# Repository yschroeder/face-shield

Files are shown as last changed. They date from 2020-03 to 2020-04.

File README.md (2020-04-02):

# Print Face Shields _the fast way_
Some files and documentation on how to print the Prusa Face Shield really fast.

## Disclaimer

These design files are provided "AS IS" WITHOUT WARRANTIES OR CONDITIONS OF ANY KIND, either express or implied, including, without limitation, any warranties or conditions of TITLE, NON-INFRINGEMENT, MERCHANTABILITY, or FITNESS FOR A PARTICULAR PURPOSE.

This not a medical device. Consider it a Halloween constume! It is neither certified nor fit for any purpose.

## TL;DR

* Use `PrusaSlicer`
* Set all speeds (except for `Support material`, `Bridges`, `Gap fill`, and `First layer speed`) to your `Travel` speed. The speeds in reality are limited by the slicer automatically by the `Max. Volumetric Speed` of the filament. So the printer will not print that fast, but as fast as possible.
* Set the `Max. Volumetric Speed` of the filament to set the real print speed. With a 0.4 mm nozzle, start at 8 mm³/s, increase to find the maximum of your printer. 17 mm³/s work for a E3D V6 with 0.8mm nozzle.
* Set 0% infill
* Set 0.87 mm extrusion width when using the `stl/Covid-19 Shield v10.stl` model
* If the extruder skips steps (loud clacking noise), lower the `Max. Volumetric Speed`. Or try to increase the nozzle temp, so the filament melts faster.

## Frequently Asked Questions

Q: That `Prusa Face Shield RC3` prints so slow and the virus is spreading exponentially! How can we be faster?

A: Good point! This is exactly the purpose of this guide/repository. I will talk you through all the important things to consider when you want to print fast.

Q: Is your improved version strong enough? [Josef Prusa said on Twitter](https://twitter.com/josefprusa/status/1242931010641244161), that we should not change the design, because it needs to be beefy.

A: Actually, I don't know. Josef Prusa was not specific on why it was designed the way it was. I think the updated version is also good, it might not be as rigid, instead it is more flexible. If you think the improved version is not strong enough, there are other options. If you want to be sure, print `stl/covid19_headband_rc3_no_text v1.stl`. That version is the orignal one without the text, so it prints a bit faster while being exactly as strong and beefy.

Take a look [here](quality_control.md) to see how you can abuse the part without breaking.

Q: How much faster can we get?

A: Here are some expected printing times calculated by `PrusaSlicer` (for a Prusa i3 MK2.5 printing PETG):

* original file with `0.20mm SPEED` settings (one of the default profiles): 3:17h
* original file with settings included in `covid19_headband_rc3_1pcs.3mf` from original web page: 2:36h
* `stl/covid19_headband_rc3_no_text v1.stl` with `0.20mm SPEED` settings (one of the default profiles): 3:12h
* `stl/Covid-19 Shield v10.stl` with optimized settings: 0:43h
* `stl/Covid-19 Shield v10.stl` with optimized settings and a 0.8mm nozzle: 0:36h
* `stl/Covid-19 Shield v18.stl` with optimized settings and a 0.8mm nozzle: 0:31h

Q: I want to print overnight and do not want to get the done print every hour or so.

A: You are in luck, there is a stackable version from 2 to 9 parts. It is easily printable with a 0.4mm nozzle in about an hour per headband. Config for Slic3r: `layer: 0.25mm, all speeds to 150mm/s, bridging speed to 50mm/s, gap fill to 0mm/s, PLA, enable detect bridging perimeters`.

Q: I am using Cura to slice my STls, can you provide a guide for Cura?

A: I am afraid that at this point, I can only provide a guide for `PrusaSlicer`. By the way: Did you know that `PrusaSlicer 2.2` supports the `Ender 3` out of the box? You might want to try that!

Q: Can you provide a 888 version for A4 sheets?

A: Short answer: Good idea, a hospital also asked us for wider shields, so we did a prototype of this. Our results were mediocre at best, thus we discarded the idea and focused on the `v18` instead. Long answer: 888 punches are not close to the edge, the sheet will not bend properly around the printed part. You could solve this with extra hooks that catch the sheet at the ends. However, this would not work with thick sheets (0.8 mm) which are currently easy to buy. The wider design needs other struts, our prototype did not bend correctly so the sheet was inpossible to get on (again, 0.8 mm). We do not want to encourage you to use laser printer A4 clear sheets or laminating film! Users reported that you get headaches and vertigo after longer use. Also you cannot work on small things (dentist, stitch a wound). Especially the laminating film has bad optical properties. Further, production of injection molded parts for the original Prusa design is ramping up and sheets for the Prusa design will become common by then. Other hole layouts would be incompatible. Lastly, we found that a 297 mm wide sheet from 0.8 mm PETG is too heavy and uncomfortable. I hope these are enough reasons to not make a A4/888 version.

Q: How do I know my print is sturdy enough?

A: Look into the [Quality Control](quality_control.md) document, there we provide some hints how your part should look like, or not look like.

Q: I guess my part failed the quality control, what can I do?

A: The [Quality Control](quality_control.md) document also gives hints on what to change. Look into it again.

## Which model to print?

This repository contains multiple models that you can choose from. Let me introduce them to you:

### `stl/covid19_headband_rc3_no_text v1.stl`
This a remix of the original [Prusa Face Shield RC3](https://www.prusaprinters.org/prints/25857-prusa-face-shield). I removed the text and indents from it as it slows down printing. Otherwise, this is exactly the same as the original.

### `stl/Covid-19 Shield v18.stl` and `stl/Covid-19 Shield v10.stl`
These are versions that I designed myself. All the relevant features have the same geometry as the original Prusa version. However, the wall thickness is reduced from 2.5 mm to 1.67 mm. This makes it possible to print it very fast, but it gets more flexible (maybe this is not even a downside). The guide below uses this model.

If you have problems with layer adhesion, try `stl/Covid-19 Shield v18 Lily.stl`. It has lily pads at crucial points to help with adhesion. Just remove them with side cutters at the end.

If you want to print for longer durations (e.g. over night), you can try the stacked versions. Look into `stl/stacks`. We have stacks from 2 to 9 parts. Start with a small stack and check if it prints well on your machine and that you can split the parts afterwards!

**ATTENTION: Make sure the two perimeters stick together well! If they don't, the finished part will be extremely weak! You can try to increase the extrusion width even further (e.g. 1.0 mm) or increase the extrusion multiplier. If you cannot manage to print parts where the two wall stick to each other, print the v10 or original RC3 instead!**

### `stl/Covid-19 Shield 2.5mm v2.stl`
If you think the above version is too flimsy/flexible you can go with this one. It has the same thickness as the original from Prusa. It has a constant wall thickness of 2.5 mm.

Note: This a sturdy version of the `v10`. I will not provide a sturdy version of `v18`, as the `v18` is sturdy enough.

### `stl/Bottom Reinforcement fast MK2 v3.stl`
This is an updated version of the original bottom reinforcement part from the Prusa shield. It has no holes and constant wall thickness of 1.67 mm as well. The original one has a 1 mm gap for the plastic sheet. This one has only 0.8 mm for a tighter fit. Make sure you plastic sheets fit into this before starting mass production!

### `stl/Bottom Reinforcement light v10.stl`
This alternative to the original bottom reinforcement part prints much faster (I can print 20 in 53 minutes). It works for all sheet thicknessnes, 0.25mm, 0.5mm, and 0.75mm were already tested successfully. If you are unsure which bottom part you should print, choose this one!

Thanks to Hackbroetchen for the idea in his original design: https://www.prusaprinters.org/prints/27801-easy-and-fast-bottom_reinforcement-alternative

## Print Settings

Overall, the model we want to print is pretty simple. We do not want it to look super nice, it needs to be functional. There is basically one parameter that limits your maximum print speed: `Max. Volumetric Speed`. This parameter is defined in `mm³/s` (cubic millimeters per second) and tells `PrusaSlicer` the maximum amount of material your hotend is able to melt per second. The exact value for this depends on your hotend, nozzle size, material, print temperature, extruder gears... So you need to experiment with this a bit. In the end it boils down to this: You want your printer to extrude the maximum amount of material _all the time_. Luckily, you don't strictly need a large nozzle to achive this (but it helps). Even printers with 0.4 mm nozzles can reach their `Max. Volumetric Speed`.

There are some types of features that slow down your 3D printer. These includes gap filling small holes (or thin spaces between narrow outer perimeters), sharp turns of the printing direction and infill (which is basically sharp turns of the printing direction all the time). If you manage to print your model by only printing perimeters you can increase your print speed a lot!

The following picture shows infill (dark red) and gap fill (white). Both are slow to print.
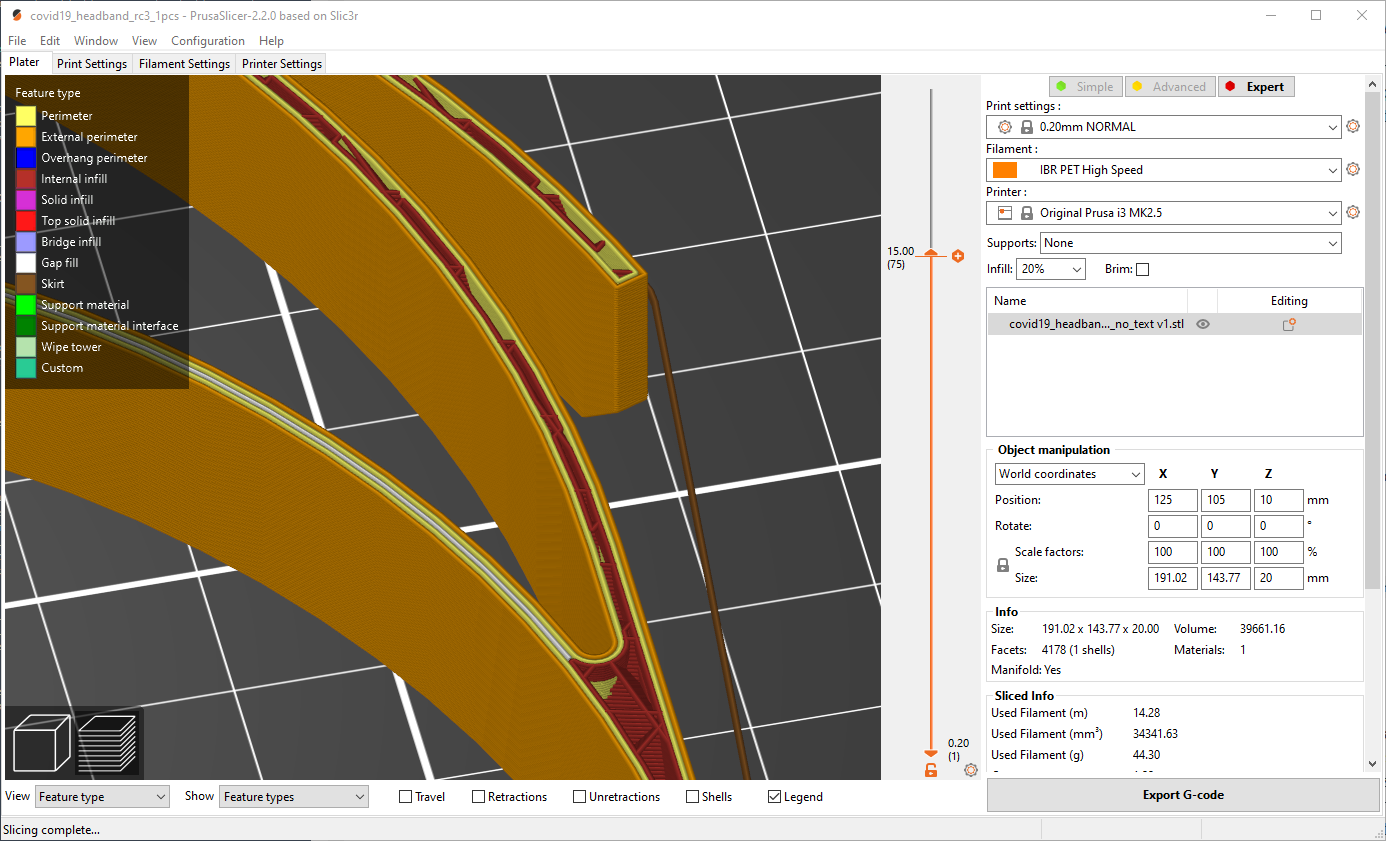
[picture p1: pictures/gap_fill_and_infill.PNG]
Gap Fill and Infill


The following picture shows a model that only consists of a single perimeter running all around the model (creating two extrusion lines). This is much faster to print (and also gives a very nice surface!).
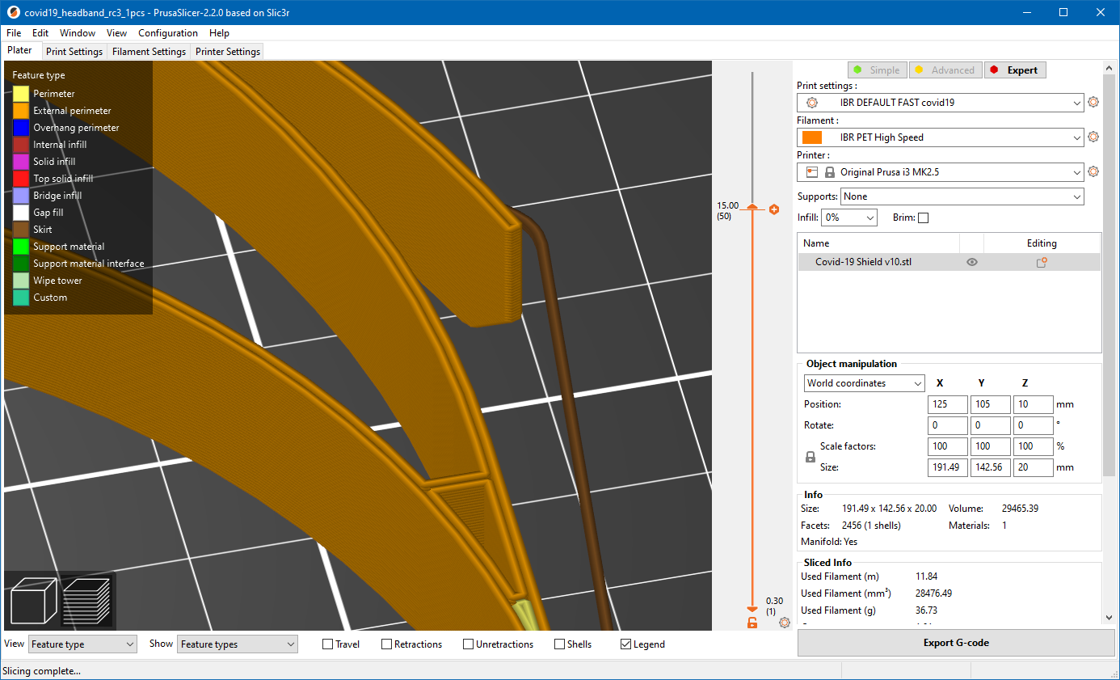
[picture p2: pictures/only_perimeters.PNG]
Only Perimeters


How can you achive this?

First, you need a model with a constant wall width and you need to know this width. The model `stl/Covid-19 Shield v18.stl` is designed to have the exact same wall thickness of 1.67 mm everywhere. If you manage that your perimeters exactly add up to 1.67 mm, no slow gap filling or infill is needed.

Second, you need to set you extrusion width correctly. Luckily, `PrusaSlicer` can help you with this. It has a function that tells you the optimal wall thickness of your model for thin wall, see the following picture:
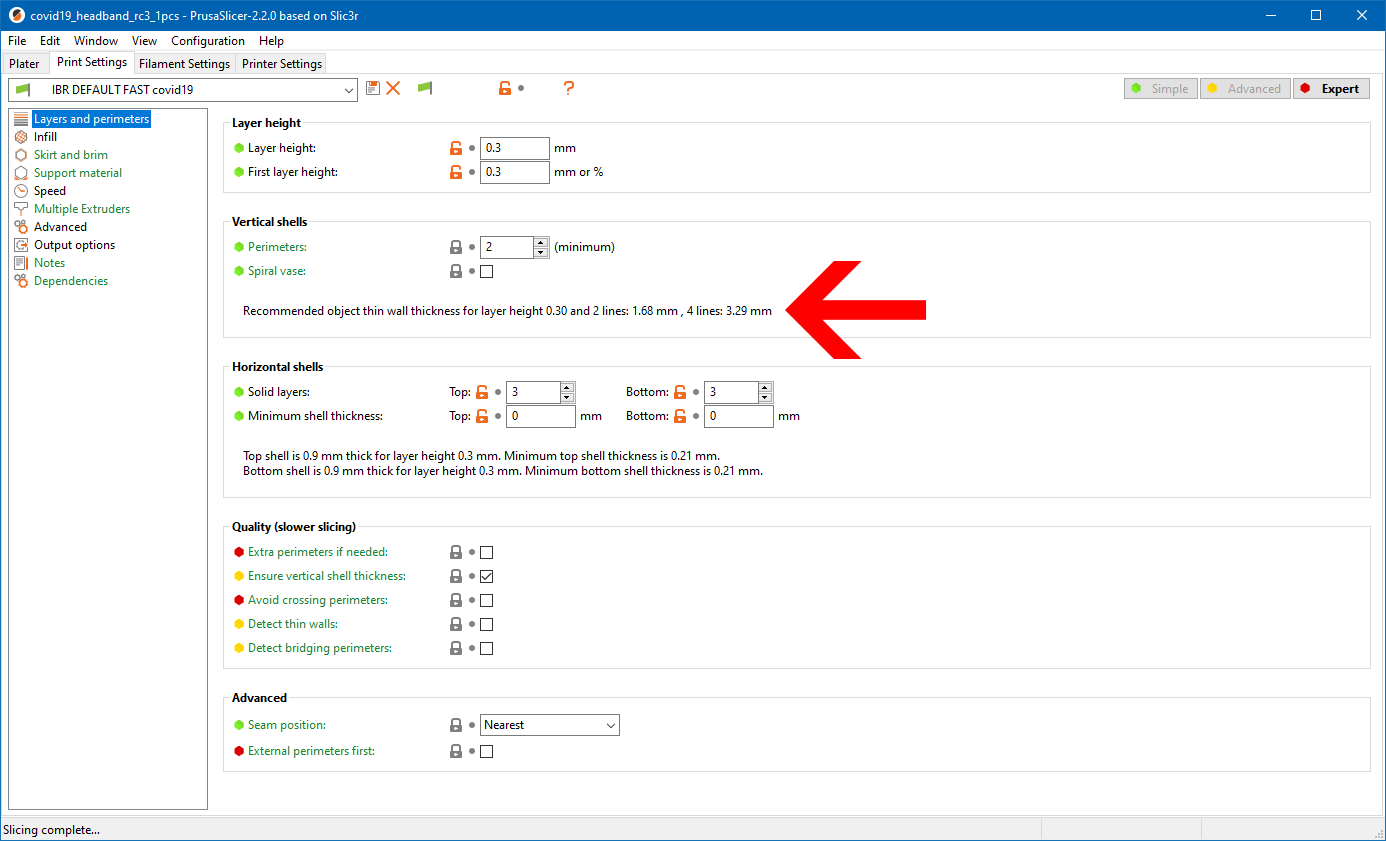
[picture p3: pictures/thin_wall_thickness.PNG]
Thin Wall Thickness


Here it says that the optimal thin wall thickness is 1.68 mm for two lines and 3.29 mm for 4 lines. 1.68 mm is very close to 1.67mm, so this is correctly configured! This value is influenced by the `Layer height` and the extrusion width for `Perimeters` and `External perimeters`. An extrusion width of 0.87 mm and a layer height of 0.3mm are used here for a 0.4 mm nozzle. Yes, you can actually print 0.87 mm width with a 0.4 mm nozzle (at least with an E3D nozzle). This [YouTube video by CNCKitchen](https://www.youtube.com/watch?v=9YaJ0wSKKHA) gives more info if you are interested.

Ok, we now have a model that is designed for this kind of print and a correct perimeter width. Let's talk about print speed. Rembember the `Max. Volumetric Speed`? This is your print speed. Configure all speeds (except for `Support material`, `Bridges`, and `Gap fill` and `First layer speed`) to your `Travel` speed. Yes, do this. You won't reach these speeds anyway (and if you actually do, can I have your printer please?). Now set the `Max. Volumetric Speed` in `Filament Settings/Advanced` to a low starting value. 8 mm³/s is a good starting point.

Let's quickly go through some other settings that can increase your print speed: The model we are printing does not need any infill. You can safely set it to 0%. Only the hooks for the rubber band would get some and they don't need it. Also, you can disable gap filling completely. Yes, this ends up with some small holes, but saves quite some time. Also it might reduce stringing, as sometimes the gap fill material does not fit into its hole and squeezes out. Disable gap fill by setting the `Gap fill` speed to 0.

Now go to the `Plater` tab and slice your model. In the bottom left corner, change the `View` to `Volumetric flow rate`. You model should have the maxum flow rate (8 mm³/s) everywhere (expect for the first layer) like in this picture:
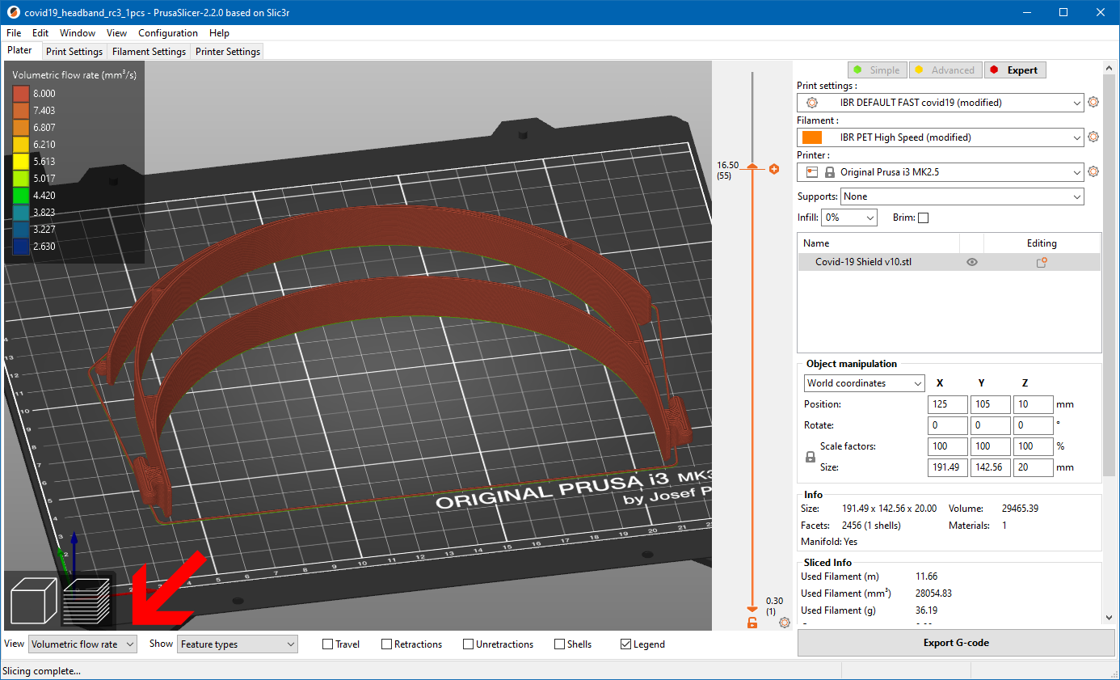
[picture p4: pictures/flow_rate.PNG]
Flow Rate


You should now be good to go for your first test print with high speed settings. If this works well (and I hope it does, otherwise this guide might be crap...) you can increase the `Max. Volumetric Speed` (e.g. in steps of 2 mm³/s) until your print starts to look ugly or your extruder makes painful noises and loses steps. If this happens, you have reached the limit of your printer. Go down to the last working value (I am running a Prusa i3 MK2.5S with a 0.8 mm nozzle at 17 mm³/s).

## Advanced Parameter Tuning

Ok, you got the basic fast print working, but you want more!

You can tune the amount of `Solid layers` at the top to close holes in the top layer of hooks for the rubber band. Increase the number of solid layers to 5. It also helps to set the `Solid infill` and `Top solid infill` to 0.55 mm, to close even more holes.

You can also tune the K factor (also known as linear advance) for your printer. Make sure it supports it. Prusa printers do support this. It will basically control the pressure in the nozzle. This is important at high speeds. You can read more about this in the [Prusa Knowledge Base](https://help.prusa3d.com/en/article/linear-advance_2252). Prusa suggest a default of 45 for PETG. I get better results with 40 on a 0.4 mm nozzle. On my 0.8 mm nozzle I am currently using a value of 15.

[gap_fill_and_infill]: pictures/gap_fill_and_infill.PNG "Gap Fill and Infill"

[only_perimeters]: pictures/only_perimeters.PNG "Only Perimeters"

[thin_wall_thickness]: pictures/thin_wall_thickness.PNG "Thin Wall Thickness"

[flow_rate]: pictures/flow_rate.PNG "Flow Rate"

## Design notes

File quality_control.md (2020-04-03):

# Quality control for face shields

Welcome to the quality control section! You being here indicates that you actually care about what you print. Congratulations!

**ATTENTION: THESE TESTS ONLY APPLY TO THE `v18` SHIELD! OTHER VERSIONS ARE LESS FLEXIBLE AND WILL POSSIBLY BREAK EARLIER!**

## What your part should look like

Actually, we can't really tell you what your printed part needs to withstand. We can only show you what our parts withstand. If your part breaks earlier, this does not automatically mean it is bad, but it is not as good as it could be! **Our part in the pictures is made from PETG, so if your part is from another material your results might be different.**

To check your part, bend it the following ways, **during bending it should not crack at all!**

Put your part on a table and press the tabs for the plastic sheet down:
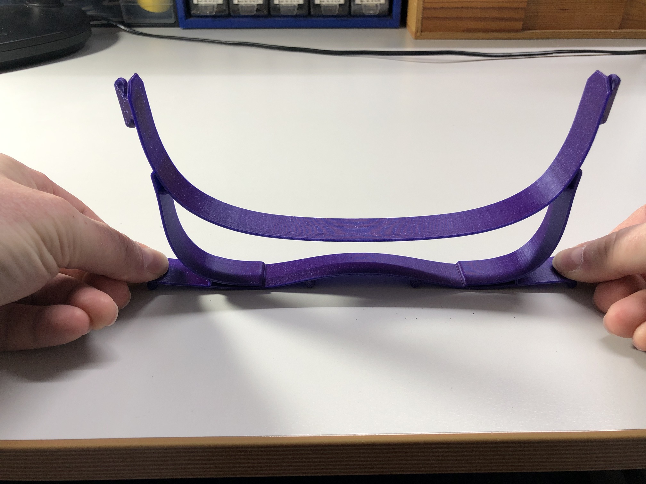
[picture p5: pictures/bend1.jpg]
Bend 1


Bend the rubber band hooks all the way to each other:
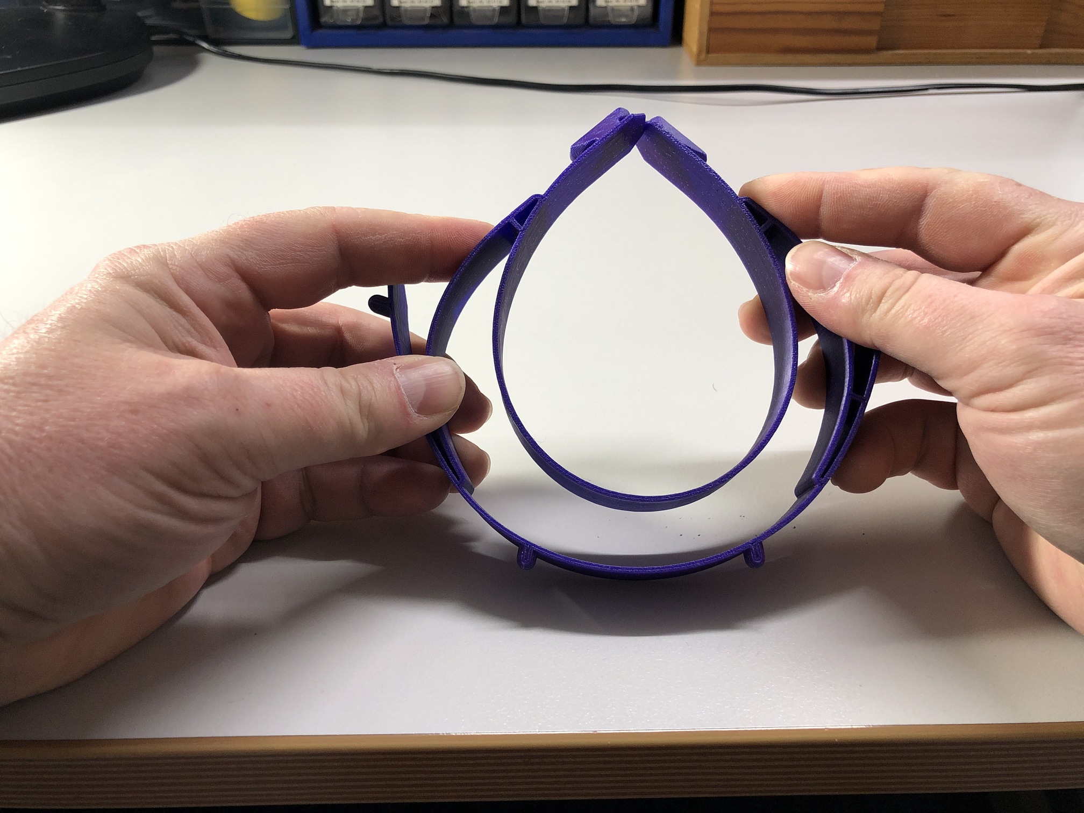
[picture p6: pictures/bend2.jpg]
Bend 2


Bend the two sides at 90° angle **in both directions multiple times**:
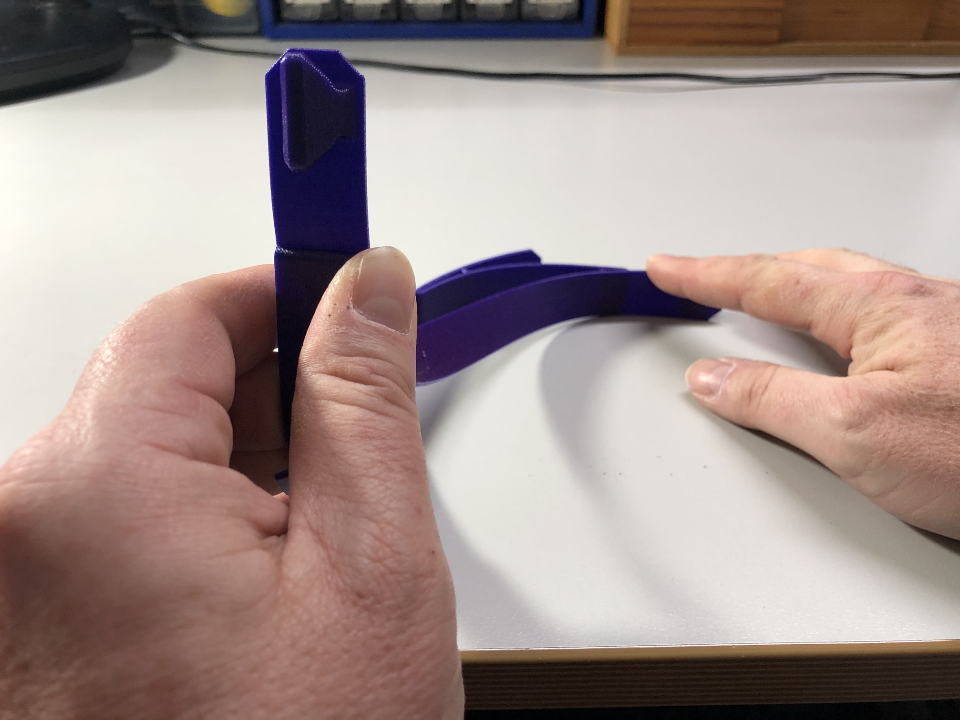
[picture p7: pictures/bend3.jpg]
Bend 3

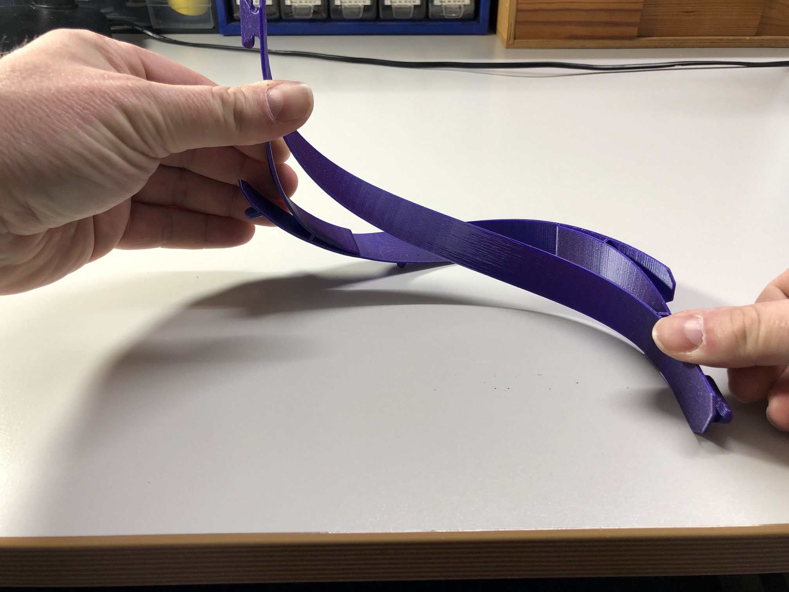
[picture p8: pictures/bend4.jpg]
Bend 4


Bend the two sides across each other:
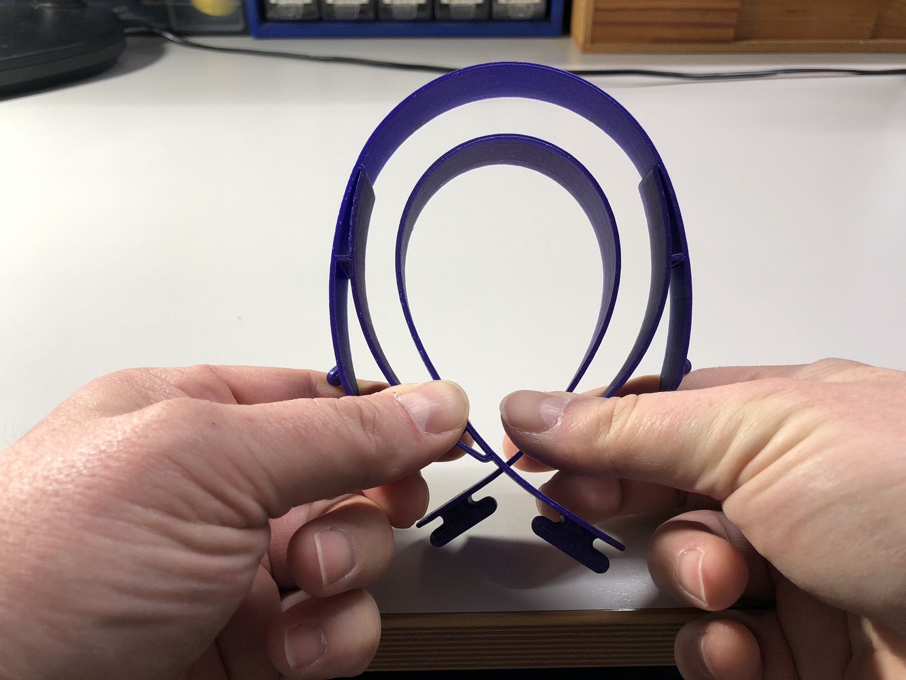
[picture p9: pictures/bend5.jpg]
Bend 5


[Here](https://cloud.stratum0.org/index.php/s/fAjpCAXFLmFsxLq?path=%2FMaterialtest%20Videos) you can find a video that shows how a PLA part can be abused if printed properly (file `PLA biegen.mp4`).

## What your part should not look like

[Here](https://cloud.stratum0.org/index.php/s/fAjpCAXFLmFsxLq?path=%2FMaterialtest%20Videos) you can find a video that shows how a good part looks in comparison to a bad part (file `qualitätstest.MOV`).

### Gaps

This part contains gaps (top two red arrows) which lead to the crumbling in the video shown above:
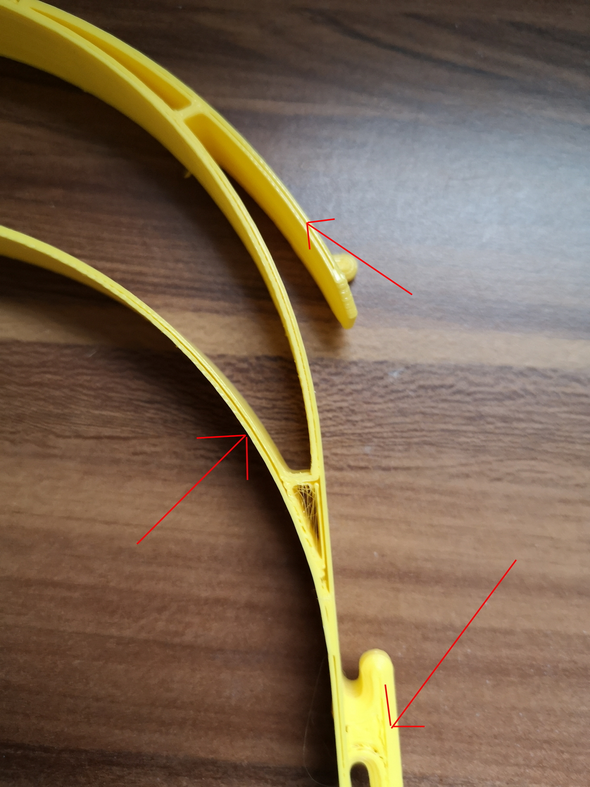
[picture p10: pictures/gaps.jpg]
Gaps


You have two options to close these gaps: In `PrusaSlicer` you can increase the `Extrusion width` of `External perimeters` even more (above 0.87 mm). `PrusaSlicer` will put the two shells closer together in this case (to reach the required 1.67 mm wall thickness). The other option is to increase the `Extrusion multiplier` so more material can fill the gap.

The problem indicated by the lower red arrow can be fixed by decreasing the `Extrusion width` for `Solid infill` and `Top solid infill` to 0.55 mm or less, depending on your nozzle size.

### Holes

You might also encounter holes in your part:
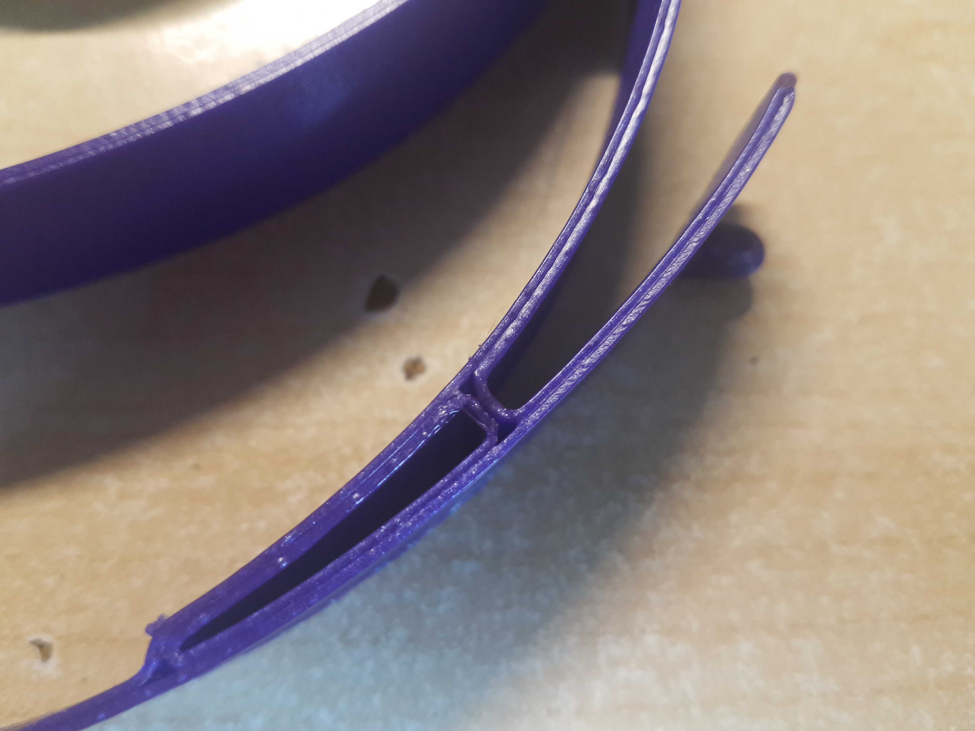
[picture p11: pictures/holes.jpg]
Holes


This effect can be reduced by increasing the `Extrusion width` of `External perimeters`. I found 1.0 mm working.

[bend1]: pictures/bend1.jpg "Bend 1"
[bend2]: pictures/bend2.jpg "Bend 2"
[bend3]: pictures/bend3.jpg "Bend 3"
[bend4]: pictures/bend4.jpg "Bend 4"
[bend5]: pictures/bend5.jpg "Bend 5"
[gaps]: pictures/gaps.jpg "Gaps"
[holes]: pictures/holes.jpg "Holes"

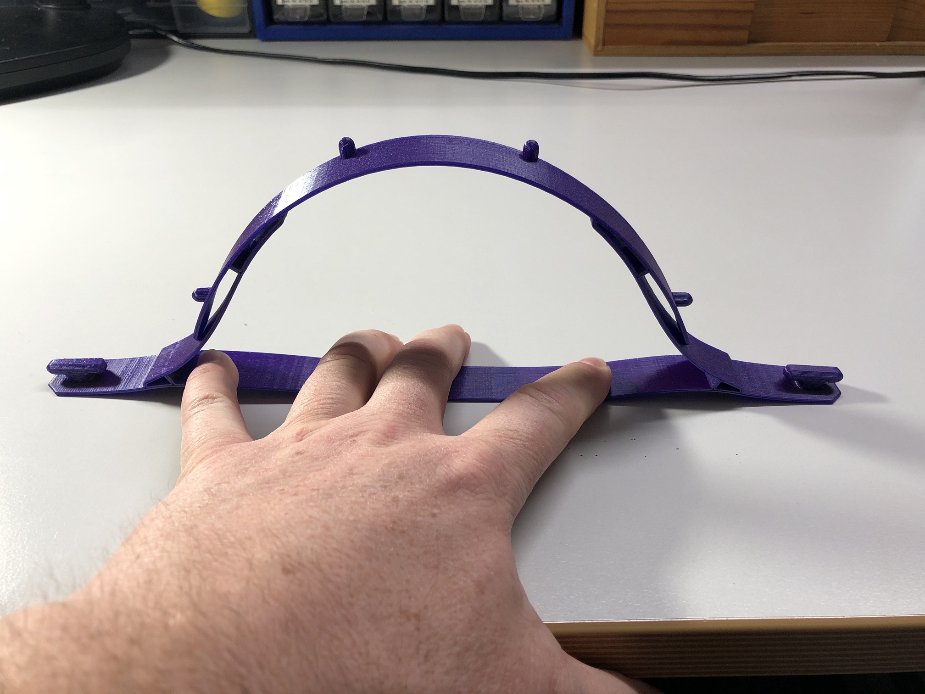
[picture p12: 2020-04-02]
pictures/bend6.jpg

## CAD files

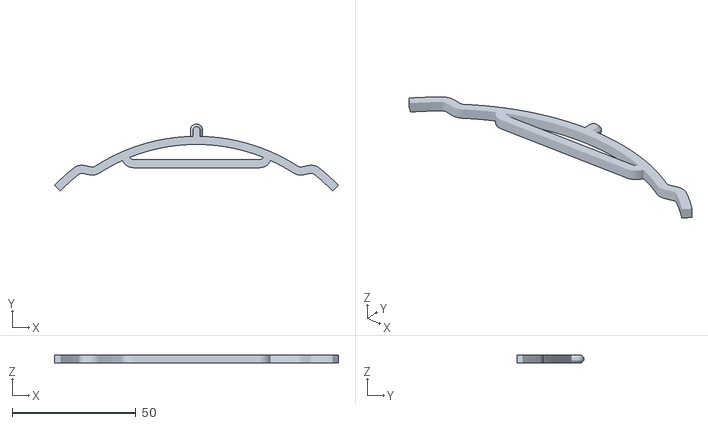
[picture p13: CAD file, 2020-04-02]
stl/Bottom Reinforcement light v10.stl
114.9 x 27.1 x 3.29

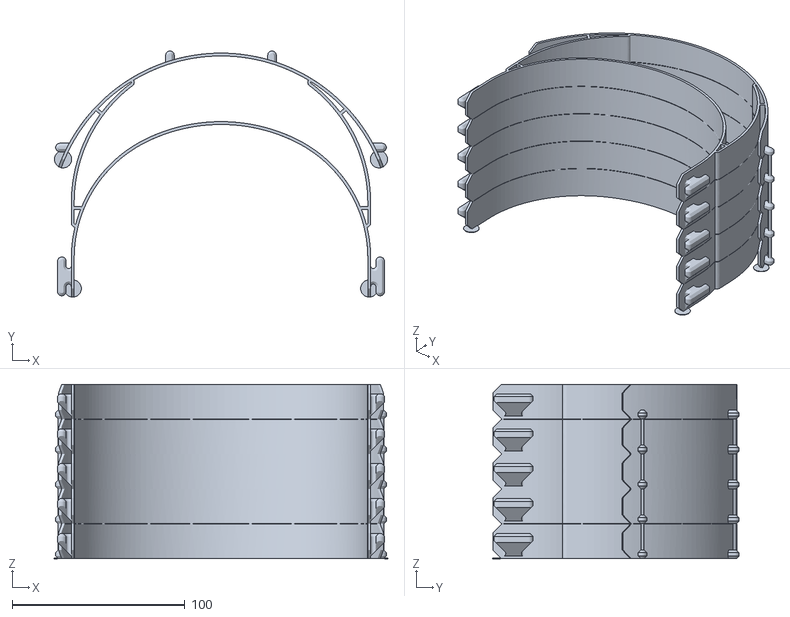
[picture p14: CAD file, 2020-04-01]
stl/stacks/v18/Covid-19 Shield v18 Stack5.stl
192.8 x 142.6 x 101.0

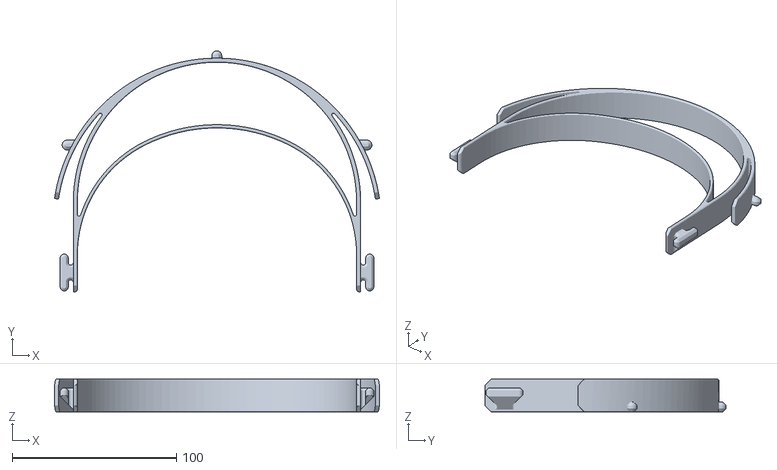
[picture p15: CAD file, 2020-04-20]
stl/US/covid19_headband_rc3us_1pc_no_text v2.stl
197.9 x 147.0 x 20.0

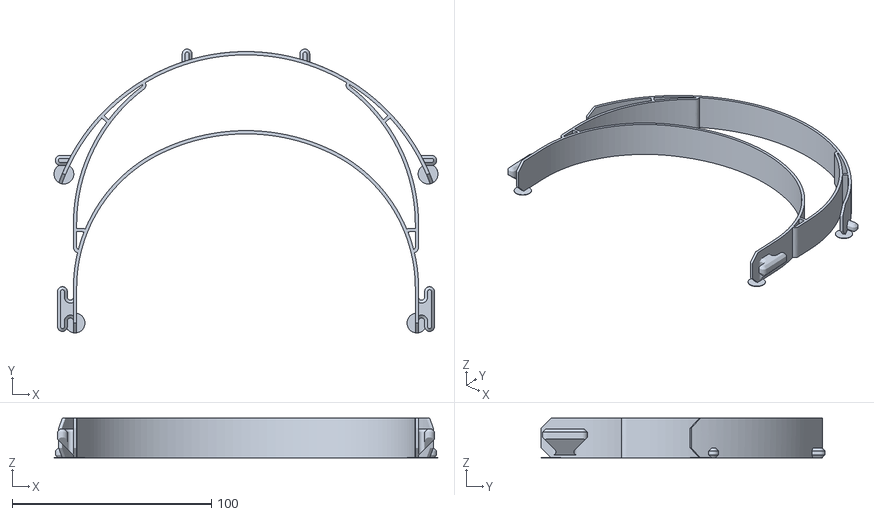
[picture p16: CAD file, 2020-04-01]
stl/Covid-19 Shield v18 Lily.stl
192.8 x 142.6 x 20.0

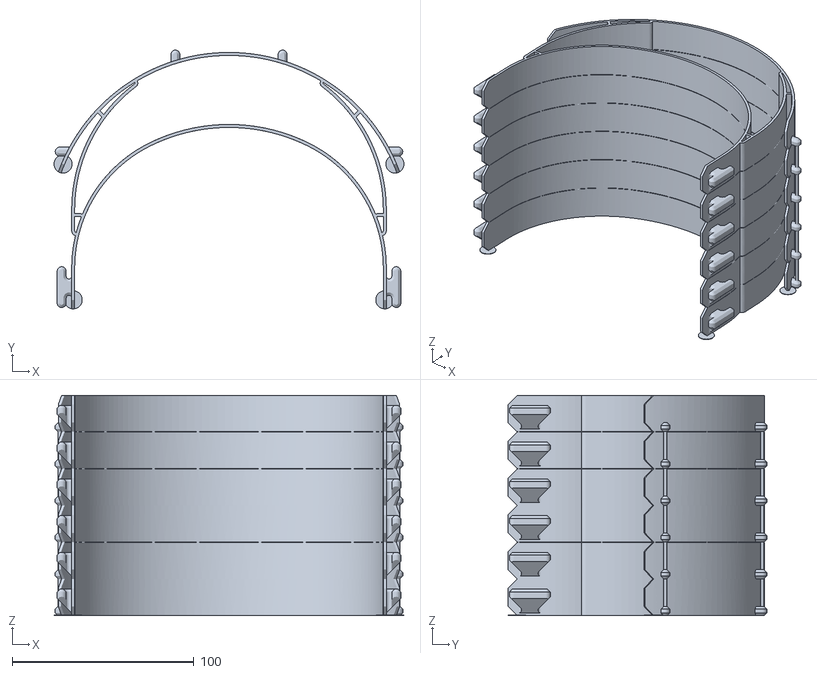
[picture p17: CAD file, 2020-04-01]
stl/stacks/v18/Covid-19 Shield v18 Stack6.stl
192.8 x 142.6 x 121.2

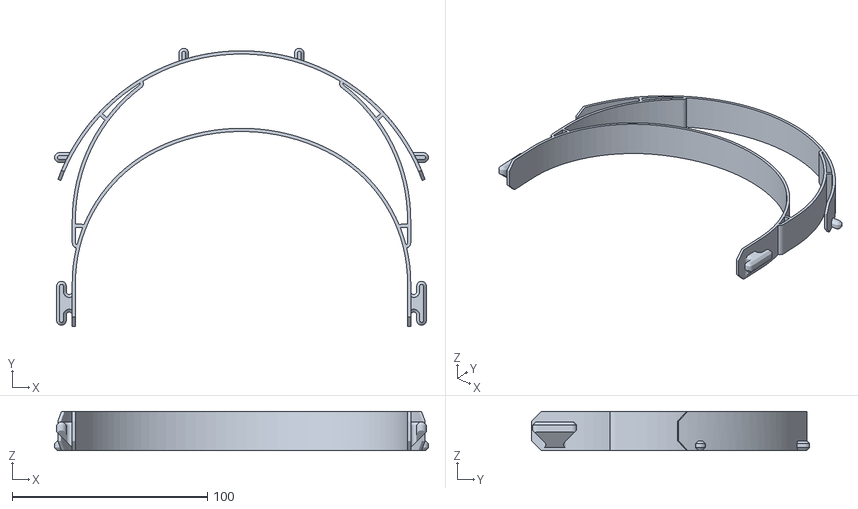
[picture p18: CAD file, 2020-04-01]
stl/Covid-19 Shield v18.stl
191.5 x 142.6 x 20.0

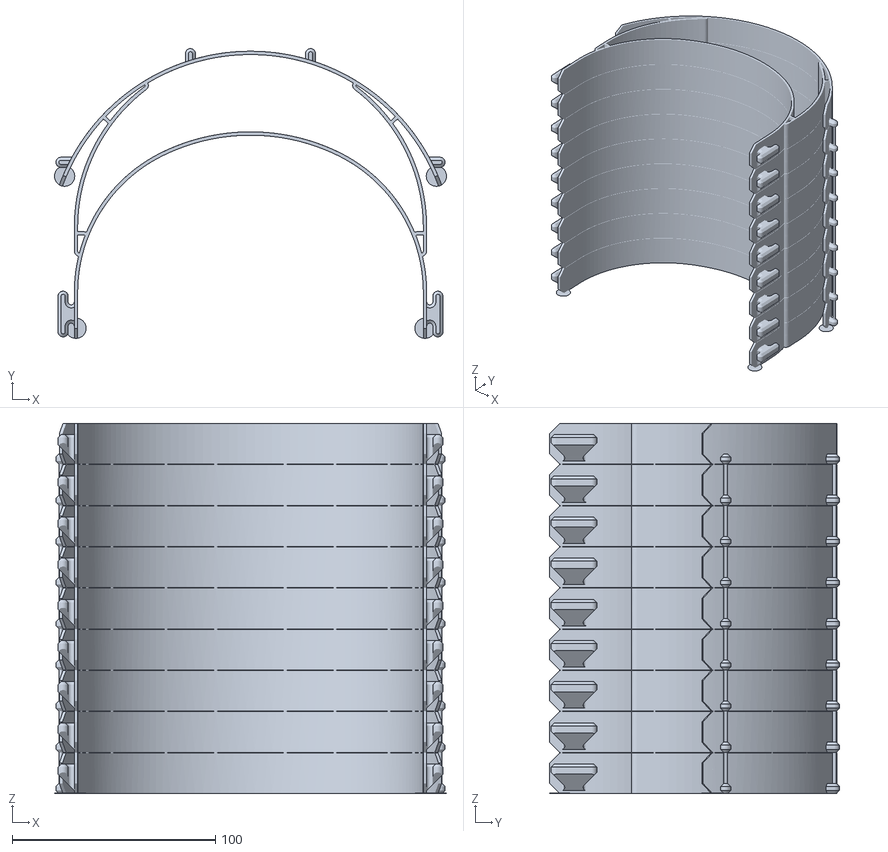
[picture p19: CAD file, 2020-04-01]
stl/stacks/v18/Covid-19 Shield v18 Stack9.stl
192.8 x 142.6 x 182.0

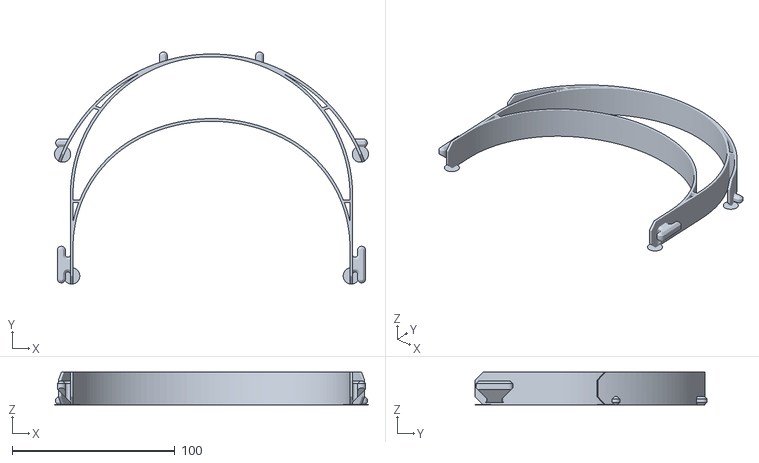
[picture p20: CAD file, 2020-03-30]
stl/Covid-19 Shield V10 Lily.stl
192.8 x 142.6 x 20.0

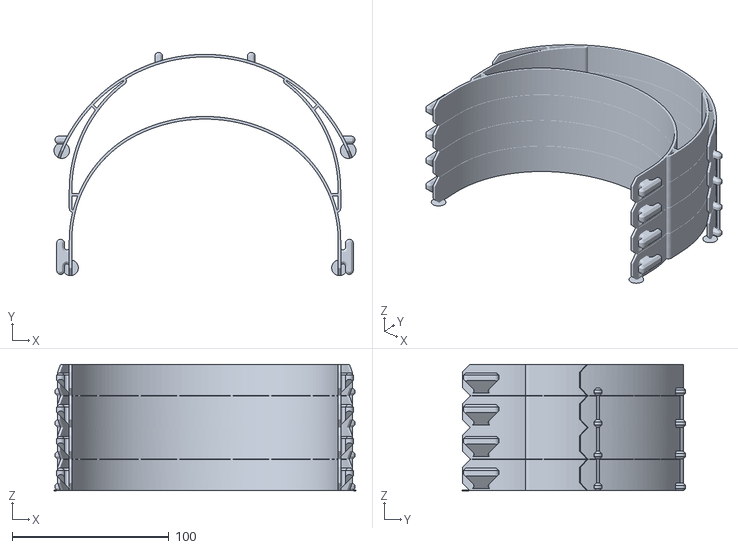
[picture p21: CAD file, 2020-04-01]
stl/stacks/v18/Covid-19 Shield v18 Stack4.stl
192.8 x 142.6 x 80.8

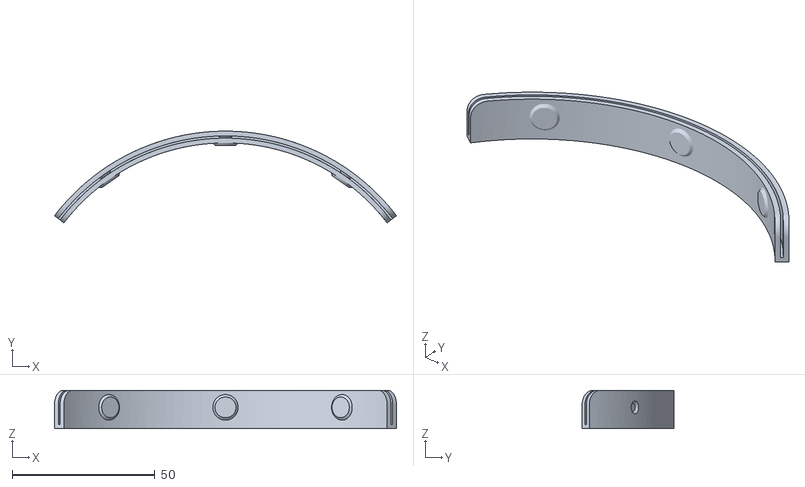
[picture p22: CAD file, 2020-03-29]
stl/Bottom Reinforcement fast MK2 v3.stl
120.0 x 32.2 x 13.5

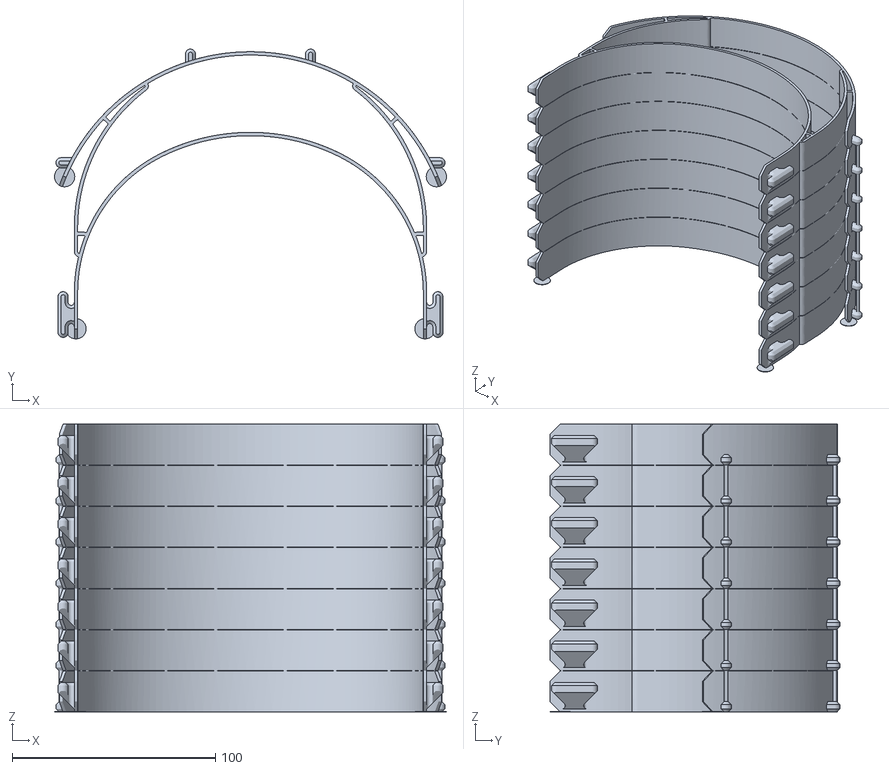
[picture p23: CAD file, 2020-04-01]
stl/stacks/v18/Covid-19 Shield v18 Stack7.stl
192.8 x 142.6 x 141.5

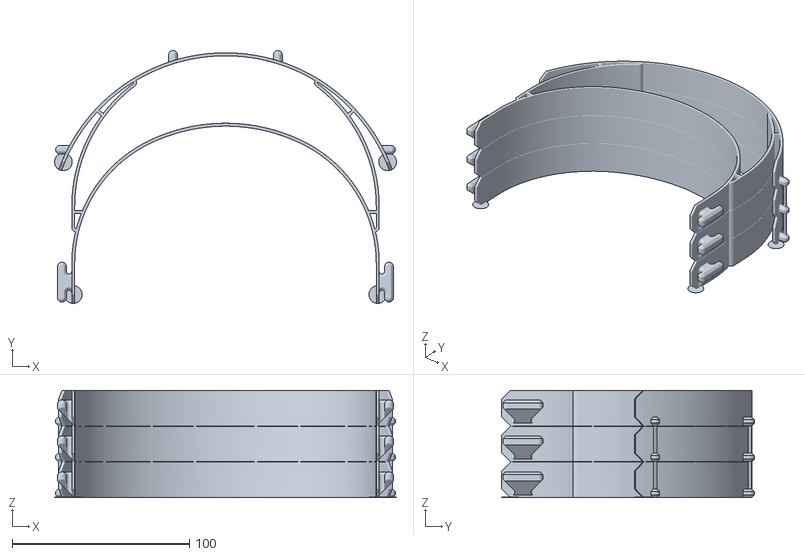
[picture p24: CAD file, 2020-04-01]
stl/stacks/v18/Covid-19 Shield v18 Stack3.stl
192.8 x 142.6 x 60.5

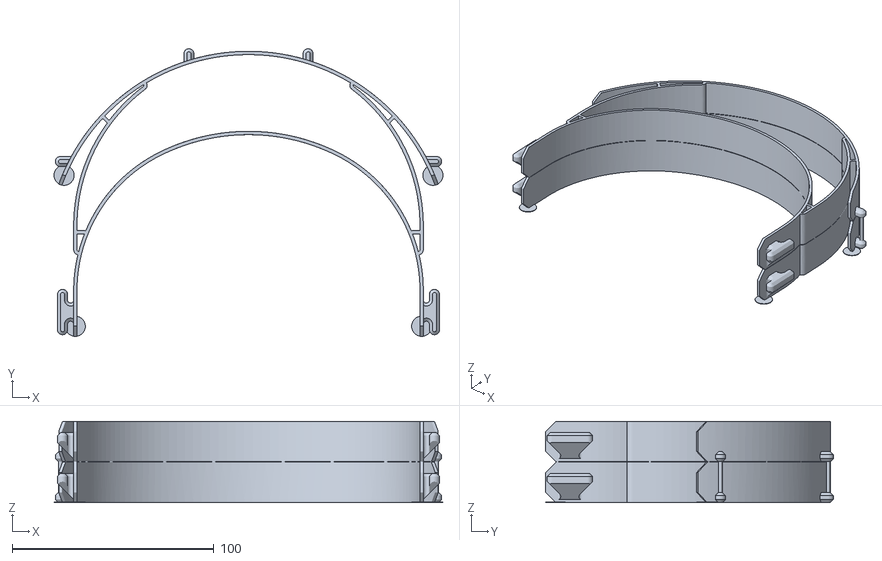
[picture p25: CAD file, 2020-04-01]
stl/stacks/v18/Covid-19 Shield v18 Stack2.stl
192.8 x 142.6 x 40.2

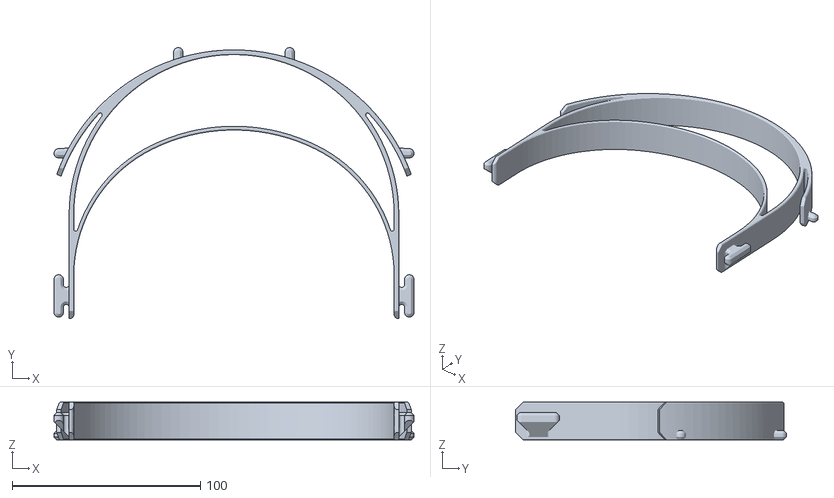
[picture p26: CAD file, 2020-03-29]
stl/covid19_headband_rc3_no_text v1.stl
191.0 x 143.8 x 20.0

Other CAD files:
stl/Covid-19 Shield 2.5mm v2.stl
stl/Covid-19 Shield v10.stl
stl/stacks/v18/Covid-19 Shield v18 Stack8.stl
stl/stacks/v10/Covid-19 Shield v10 Stack4.stl
stl/stacks/v10/Covid-19 Shield v10 Stack2.stl
stl/stacks/v10/Covid-19 Shield v10 Stack3.stl
stl/stacks/v10/Covid-19 Shield v10 Stack5.stl
stl/stacks/v10/Covid-19 Shield v10 Stack6.stl
stl/stacks/v10/Covid-19 Shield v10 Stack7.stl
stl/stacks/v10/Covid-19 Shield v10 Stack8.stl
stl/stacks/v10/Covid-19 Shield v10 Stack9.stl

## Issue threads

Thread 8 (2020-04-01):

### ISSUE TITLE
Stapel STL fehlerhaft

### ISSUE THREAD

**Issue by joerg900** [yschroeder/face-shield#8]
Simplify3d, Cura laden die Stapel-STLs nicht, aufgrund eines Fehlers in der Datei.

| Slicer |                        Fehlermeldung                        |
|--------|-------------------------------------------------------------|
| S3D    | Error importing STL file. incorrect binary format detected. |
| Cura   | Invalid File                                                |
                                             |

**Comment by vBJohannes** [comment]
Welcher der Stapel-Dateien? Ist das eventuell mit dem Fix aus #6 bereits behoben?

**Comment by joerg900** [comment]
Bei allen Dateien, habe den aktuellsten Stand vor Erstellung des Issues geladen. Laut Commit-Kommentar war das nach dem Fix aus #6.

**Comment by vBJohannes** [comment]
S3D kann ich nicht testen. Mit UltimakerCura4.5.0 lassen sich alle Stacks per Drag-and-Drop importieren und slicen. Slicing dauert zwar lange, aber ich bekomme bei keinem Stapel Fehler.
Hier beispielhaft der 7er Stapel.
![grafik](https://user-images.githubusercontent.com/9631621/78146666-c0cbf400-7432-11ea-9966-892192077cfe.png)

**Comment by joerg900** [comment]
Der Fehler lag bei mir. "Rechtsklick-->Ziel speicher unter..." führt nicht wie erwartet zum Download des Modells, sondern zu einer .STL-Datei, die den HTML Inhalt der Seite beinhaltet.

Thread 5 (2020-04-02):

### ISSUE TITLE
888 version

### ISSUE THREAD

**Issue by thoka** [yschroeder/face-shield#5]
Could you provide a version with standard 80-80-80 distance between the holders? 
This would enable easy punching of a4 sheets with a common double-puncher.

For simple shields a total height of 11mm seems to be enough. 
So this could be a fast to print lightweight design.

**Comment by yschroeder** [comment]
There are already 888 versions avaialable as remix of the original one AFAIK. I might try to create my optimized version as 888, but I won't find the time today...

**Comment by yschroeder** [comment]
We decided to not make an 888 version. The reasons can be found in the FAQ of the README.

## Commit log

2020-03-29 Add Prusa Protective Face Shield RC3 without text
    This version is exactly the original Prusa design, but without the text
    and other indents. This prints faster, especially on printers with low
    acceleration speeds.
    [covid19_headband_rc3_no_text v1.stl]
2020-03-29 Add improved RC3 Face Shield
    This version has 1.67 mm wall thickness (while the original has 2.5 mm).
    It can be printed without infill when the perimeter thickness is
    correctly configured. Check the README.md for details on how to
    configure your printer correctly!
    [Covid-19 Shield v10.stl]
2020-03-29 Add improved RC3 Face Shield with original wall thickness
    This version has the original wall thickness of 2.5 mm like the original
    Prusa Protective Face Shield RC3. You can print this if you fear that
    the other optimized version is too flimsy.
    [Covid-19 Shield 2.5mm v2.stl]
2020-03-29 Add improved Bottom Reinforcement for the RC3 Face Shield
    This version has no holes and a constant wall thickness everywhere. It
    prints faster than the original one. The slot for the plastic sheet is
    0.8 mm instead of the original 1.0 mm in this version, so check if your
    material fits in, before printing tons of this!
    [Bottom Reinforcement fast MK2 v3.stl]
2020-03-29 Add flow rate picture
2020-03-30 Add stacked versions of "Covid-19 Shield v10"
    - Version for 2 - 9 stacked headbands (just under 200mm height).
    - Few contact points between individual headbands.
    - Lily pads on a few critical points to improve adhesion.
    - Break-away support for studs.
    [Covid-19 Shield v10 Stack2.stl, Covid-19 Shield v10 Stack3.stl, Covid-19 Shield v10 Stack4.stl, Covid-19 Shield v10 Stack5.stl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]
2020-03-30 Add a single Headband with Lily Pads for more Adhesion
    [Covid-19 Shield V10 Lily.stl]
2020-03-30 Add full print bed of bottom reinforcement parts
    This file contains 46 of the bottom reinforcement parts.
    Needed print bed size is 209 x 242 mm.
2020-03-30 Clarify TL;DR
    It looked like this works only with a 0.8 mm nozzle.
2020-04-01 Fix manifold Issues with stacked Headbands
    Closes #6
    [Covid-19 Shield v10 Stack2.stl, Covid-19 Shield v10 Stack3.stl, Covid-19 Shield v10 Stack4.stl, Covid-19 Shield v10 Stack5.stl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]
2020-04-01 Add v18, an improved version of v10
    This version contains no acute angles anymore.
    It prints faster and has less holes in the end.
    [Covid-19 Shield v18.stl]
2020-04-01 Move v10 Stacks to dedicated Folder to avoid Confusion
    [Covid-19 Shield v10 Stack2.stl, Covid-19 Shield v10 Stack3.stl, Covid-19 Shield v10 Stack4.stl, Covid-19 Shield v10 Stack5.stl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]
2020-04-01 Add a single Headband v18 with Lily Pads for more Adhesion
    [Covid-19 Shield v18 Lily.stl]
2020-04-01 Add stacked versions of Shield v18
    - Fewer contact points between individual headbands than in v10.
    - Reduced amount of lily pads.
    [Covid-19 Shield v18 Stack2.stl, Covid-19 Shield v18 Stack3.stl, Covid-19 Shield v18 Stack4.stl, Covid-19 Shield v18 Stack5.stl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]
2020-04-02 Add light bottom reinforcement part
    This design is compatible with the original Prusa RC3 plastic sheet.
    Tested with 0.5mm and 0.75mm sheets.
    Remix from this design: https://www.prusaprinters.org/prints/27801-easy-and-fast-bottom_reinforcement-alternative
    Thanks to Hackbroetchen for the idea!
    [Bottom Reinforcement light v10.stl]
2020-04-02 Add section to warn about weak prints
2020-04-20 add US version of headband without text
    [covid19_headband_rc3us_1pc_no_text v2.stl]
